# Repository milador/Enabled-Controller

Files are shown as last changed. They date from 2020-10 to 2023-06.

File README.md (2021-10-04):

# Enabled Controller

Enabled Controller Wireless is an open-source switch interface that enables those with limited or no hand movement to be able to use Adaptive switches and analog joysticks as inputs to operate their computers, smartphones, and game consoles.

<p align="center">
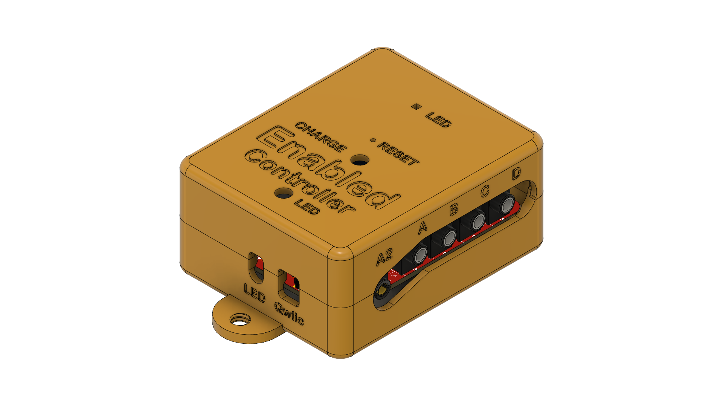
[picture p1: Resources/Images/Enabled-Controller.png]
Enabled Controller

</p>

The device offers up to eight switch input enclosures through eight 3.5mm audio jacks and four analog inputs through two 3.5mm headphone jacks. The two 3.5mm headphone jacks can be used to connect up to two X-Y analog joysticks.

The internal RGB led of ItsyBitsy and external NeoPixel is used to provide visual feedback for each action.

## Assembly Instructions Manual

The <a href="https://github.com/milador/Enabled-Controller/blob/master/Documentation/Build_Manuals/Enabled_Controller_Instructions_Manual.pdf">Assembly Instructions Manual</a> is available to download.

## User Manual

### Enabled Controller USB User Manual

<a href="https://github.com/milador/Enabled-Controller/blob/master/Documentation/User_Manuals/Enabled_Controller_USB_User_Manual.pdf">Enabled_Controller_USB_User_Manual.pdf</a>

### Enabled Controller Joystick User Manual 

<a href="https://github.com/milador/Enabled-Controller/blob/master/Documentation/User_Manuals/Enabled_Controller_Joystick_User_Manual.pdf">Enabled_Controller_Joystick_User_Manual.pdf</a>

## Parts

The <a href="https://github.com/milador/Enabled-Controller/blob/master/Components/Enabled_Controller_BOM.csv">BOM</a> file is available to download.

## Software

### Enabled_Controller_USB_Software.ino  

The <a href="https://raw.githubusercontent.com/milador/Enabled-Controller/master/Software/Arduino/Enabled_Controller_USB_Software/Enabled_Controller_USB_Software.ino">Enabled_Controller_USB_Software.ino</a> allows you to use adaptive switches as input method via keyboard/mouse HID profiles. 

### Enabled_Controller_Joystick_Software.ino  

The <a href="https://raw.githubusercontent.com/milador/Enabled-Controller/master/Software/Arduino/Enabled_Controller_Joystick_Software/Enabled_Controller_Joystick_Software.ino">Enabled_Controller_Joystick_Software.ino</a> allows you to use adaptive switches as input method via joystick HID profiles. 

## Hardware 

### PCB Design 

The <a href="https://github.com/milador/Enabled-Controller/tree/master/Hardware/PCB">PCB files</a> including both PCB Eagle design files and generated gerber files are available to download.

Front PCB:
<p align="center">
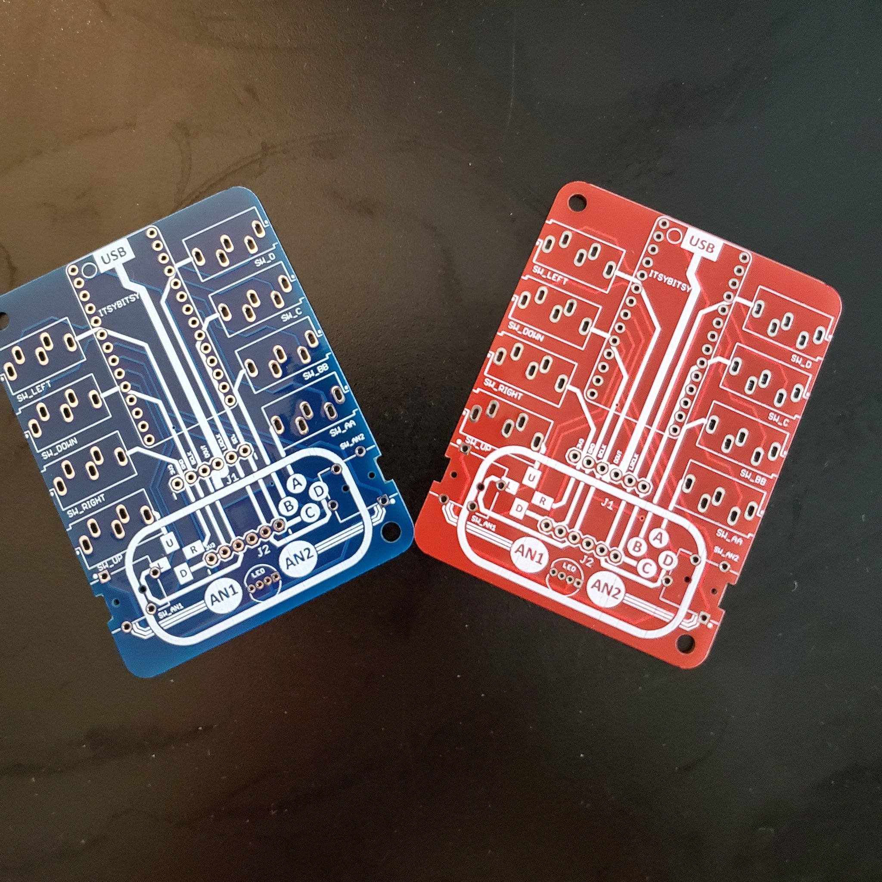
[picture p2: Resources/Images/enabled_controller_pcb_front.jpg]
Front PCB

</p>

Back PCB:
<p align="center">
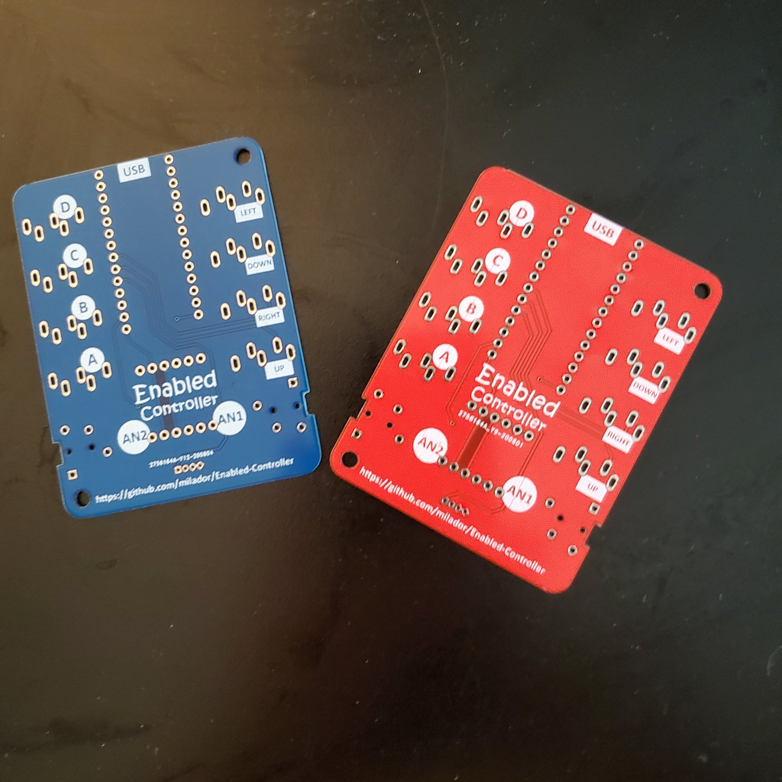
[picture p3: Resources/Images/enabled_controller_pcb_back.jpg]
Back PCB

</p>

Assembled:
<p align="center">
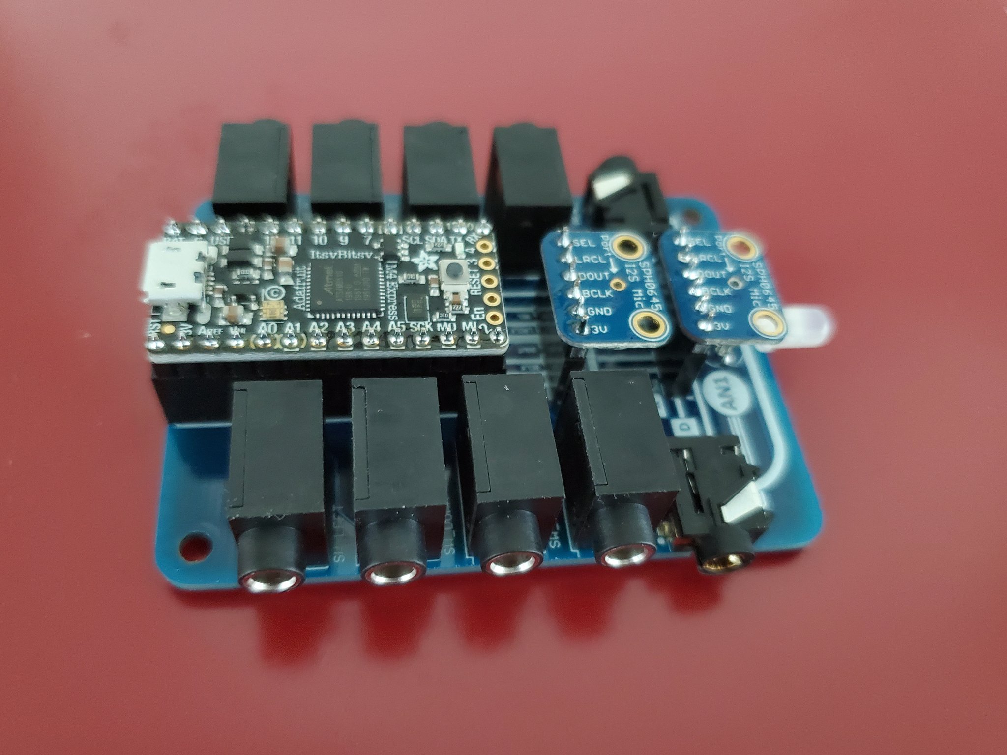
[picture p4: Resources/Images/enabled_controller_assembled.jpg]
Assembled PCB

</p>

Assembly Animation:

https://www.youtube.com/watch?v=7AMCL-cITrQ

### Enclosure

The <a href="https://github.com/milador/Enabled-Controller/tree/master/Hardware/Enclosure">Enclosure files</a> including both STL and STEP enclosure files are available to download.

<p align="center">
Enabled Controller
</p>

## License

### Creative Commons Attribution-NonCommercial-ShareAlike (CC-BY-NC-SA)

Copyright (c) 2020 Milador

A creative commons license that bans commercial use and requires you to release any modified works under this license.

<p align="center">
CC-BY-NC-SA
</p>

<br />This work is licensed under a <a rel="license" href="http://creativecommons.org/licenses/by-nc-sa/3.0/">Creative Commons Attribution-NonCommercial-ShareAlike 3.0 Unported License</a>.

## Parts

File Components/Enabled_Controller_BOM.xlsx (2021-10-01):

Index | Quantity | Digikey Part Number | Manufacturer Part Number | Description | Price (CAD) | Unit Price (CAD) | Link
1 | 1 | 1528-2554-ND | 3727 | ITSYBITSY M0 EXPRESS ATSAMD21 | 16.15 | 16.15 | https://www.digikey.ca/en/products/detail/adafruit-industries-llc/3727/8346575
2 | 1 | 1568-1213-ND | COM-12986 | ADDRESS LED DISC SER RGB 5MM 5PC | 3.99 | 3.99 | https://www.digikey.ca/en/products/detail/COM-12986/1568-1213-ND/5673799
3 | 2 | S7047-ND | PPPC141LFBN-RC | CONN HDR 14POS 0.1 GOLD | 1.28 | 1.28 | https://www.digikey.ca/en/products/detail/PPPC141LFBN-RC/S7047-ND/810186
4 | 8 | CP1-3535NG-ND | SJ1-3535NG | CONN JACK STEREO 3.5MM R/A | 1.61 | 1.61 | https://www.digikey.ca/product-detail/en/cui-inc/SJ1-3535NG/CP1-3535NG-ND
5 | 2 | CP-43514-ND | SJ-43514 | CONN JACK 4COND 3.5MM | 1.43 | 1.43 | https://www.digikey.ca/en/products/detail/SJ-43514/CP-43514-ND/368146
6 | 2 | 36-4708-ND | 4708 | HEX NUT 0.217" STEEL M3 | 0.23 | 0.23 | https://www.digikey.ca/en/products/detail/keystone-electronics/4708/4499301
7 | 2 | 335-1148-ND | RM3X10MM 2701 | MACH SCREW PAN HEAD PHILLIPS M3 | 0.92 | 0.92 | https://www.digikey.ca/en/products/detail/apm-hexseal/RM3X10MM-2701/3712296
8 | 1 | PRT-14417-ND | PRT-14417 | QWIIC JST CONNECTOR - SMD 4-PIN | 0.68 | 0.68 | https://www.digikey.ca/en/products/detail/sparkfun-electronics/PRT-14417/7652746
 |  |  |  |  | Total Price (CAD) | 41.42

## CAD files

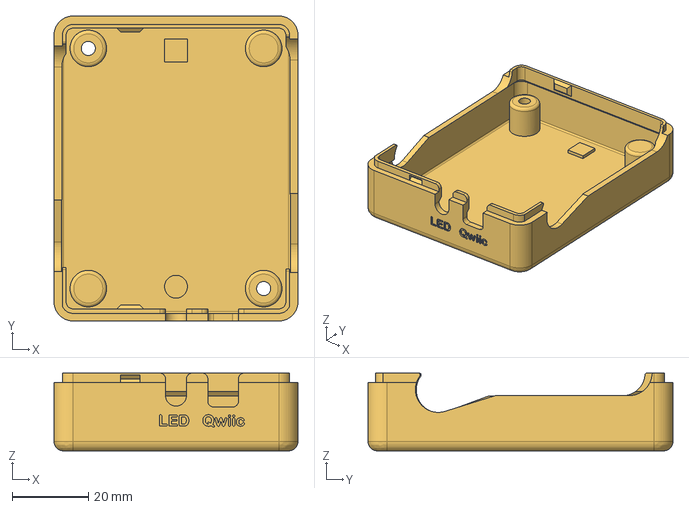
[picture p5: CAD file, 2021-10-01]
Hardware/Enclosure/STEP/Enabled_Controller_Bottom.step
64.0 x 80.0 x 20.4 mm

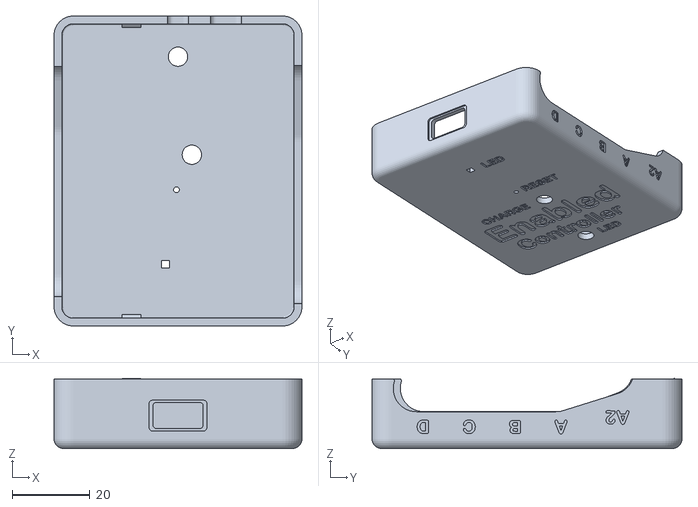
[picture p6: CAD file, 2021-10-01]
Hardware/Enclosure/STL/Enabled_Controller_Top.stl
64.0 x 80.0 x 18.1

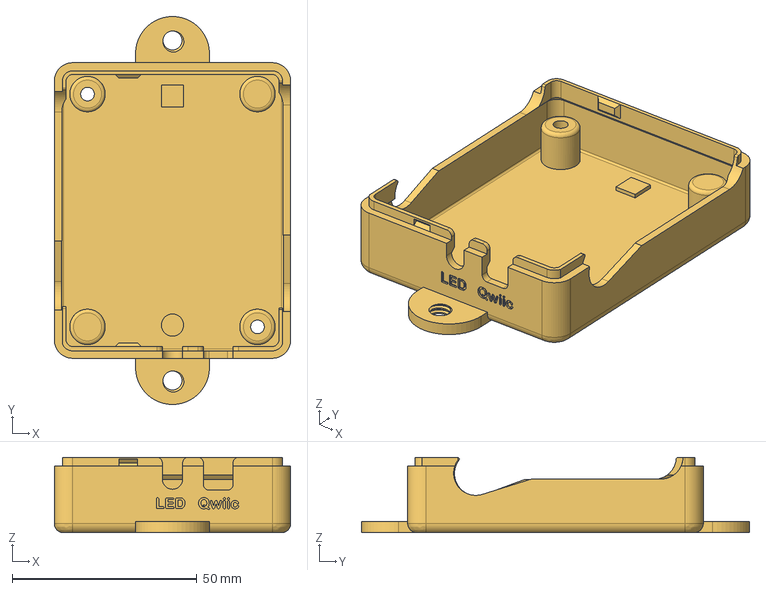
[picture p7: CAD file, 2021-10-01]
Hardware/Enclosure/STEP/Enabled_Controller_Bottom_With_Mount.step
64.0 x 105.0 x 20.4 mm

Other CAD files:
Hardware/Enclosure/STL/Enabled_Controller_Bottom.stl
Hardware/Enclosure/STL/Enabled_Controller_Bottom_With_Mount.stl

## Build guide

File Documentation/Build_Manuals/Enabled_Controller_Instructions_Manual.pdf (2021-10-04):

# ENABLED-CONTROLLER INSTRUCTIONS MANUAL

An Accessible Adaptive Switch Interface

## Version 1.2

https://github.com/milador/Enabled-Controller

1

## Contents

Components List | 2
Software | 3
Installing Arduino IDE | 3
Installing Arduino Libraries | 3
USB Version | 3
Board Support Packages | 3
Required Software and libraries | 4
Uploading Software | 5
Joystick Version | 6
Board Support Packages | 6
Required Software and libraries | 6
Uploading Software | 7
Hardware Assembly | 8
Printed circuit Board design | 8
Enclosure design | 8
Enabled-Controller Assembly | 9
Joystick Assembly | 36

2

## Components List

### 1. ADAFRUIT ITSY-BITSY M0 EXPRESS x 1

### 2. ADDRESS LED DISC SER RGB 5MM x 1

3. 14 POSITION HEADER x 2

### 4. CONN JACK STEREO 3.5MM R/A x 8

### 5. CONN JACK 4COND 3.5MM x 2

### 6. HEX NUT 0.217" STEEL M3 x 2

### 7. MACH SCREW PAN HEAD PHILLIPS M3 x 2

### 8. QWIIC JST CONNECTOR - SMD 4-PIN x 1

The bill of materials can also be downloaded from GitHub repository under main directory.

https://github.com/milador/Enabled-

Controller/blob/master/Components/Enabled_Controller_BOM.csv (https://github.com/milador/Enabled-Controller/blob/master/Components/Enabled_Controller_BOM.csv)

3

## Software

The Enabled-Controller USB software can be downloaded from the GitHub repository under software directory.

https://github.com/milador/Enabled-Controller/tree/master/Software/Arduino

The Enabled-Controller USB software is offered in the following flavors:

### 1. USB Version: Adafruit ItsyBitsy M0 Express

### 2. Joystick Version: Adafruit ItsyBitsy M0 Express

### Installing Arduino IDE

The Arduino IDE is required to compile and upload the source code to the MCU in your Adafruit ItsyBitsy board. You can download and install the Arduino from official Arduino website that you can find using following link:

https://www.arduino.cc/en/software

### Installing Arduino Libraries

The following instructions on how to install additional Arduino libraries helps you to get started with setting up Arduino IDE with required libraries and dependencies.

https://www.arduino.cc/en/guide/libraries

### USB Version

Board Support Packages
You can find the official instructions to install Board Support Packages on Adafruit website using following link:

https://learn.adafruit.com/introducing-itsy-bitsy-m0/setup

Alternatively, you can perform following instructions to install Board Support Packages:

1. Open and start the Arduino IDE.
2. Go to File > Preferences.

### 3. Add following link as a new line under Additional Board Manager URLs

- https://www.adafruit.com/package_adafruit_index.json

### 4. Restart the Arduino IDE 5. Open the Boards Manager option from the Tools > Board menu and install Adafruit SAMD

Boards by Adafruit
6. Wait until the IDE finishes installing the cross-compiling toolchain and tools associated with Board Support Package. This may take few minutes.
7. That’s it! The installation of Board Support Packages is finished.

4

Required Software and libraries
The USB version of the software requires the following files and libraries:
- StopWatch library (https://github.com/RobTillaart/Stopwatch_RT)
- EasyMorse library (https://github.com/milador/EasyMorse)
- Adafruit_NeoPixel library (https://github.com/adafruit/Adafruit_NeoPixel)
- Enabled_Controller_USB_Software.ino (https://raw.githubusercontent.com/milador/Enabled-Controller/master/Software/Arduino/Enabled_Controller_USB_Software/Enabled_Controller_USB_Software.ino)

StopWatch library helps to calculate the reaction time and timeout in the morse code interface.

The EasyMorse library is used to enable the end user to use morse code or a sequence of dots and dashes as input method.

Enabled-Controller is using Adafruit_NeoPixel library to provide visual feedback using RGB LED.

You can use the following instructions to download and install the required libraries:

1. Visit the StopWatch library (https://github.com/RobTillaart/Stopwatch_RT) github repository page.
2. Click on Code > Download Zip to download StopWatch library.

### 3. Extract Stopwatch_RT-master.zip file 4. Rename Stopwatch_RT-master folder to Stopwatch folder under Stopwatch_RT-master

subdirectory.
5. Copy or move Stopwatch folder to Arduino installation library subdirectory. As an example: This is found under C:\Program Files (x86)\Arduino\libraries in windows 10.
6. Visit the EasyMorse library (https://github.com/milador/EasyMorse) github repository page.
7. Click on Code > Download Zip to download EasyMorse library.

### 8. Extract EasyMorse.zip file

9. Rename EasyMorse-master folder to EasyMorse folder under EasyMorse-master subdirectory.
10. Copy or move EasyMorse folder to Arduino installation library subdirectory. As an example: This is found under C:\Program Files (x86)\Arduino\libraries in windows 10.
11. Visit the Enabled_Controller_USB_Software.ino (https://raw.githubusercontent.com/milador/Enabled-Controller/master/Software/Arduino/Enabled_Controller_USB_Software/Enabled_Controller_USB_Software.ino) raw source code file under Enabled-Controller github repository page.

### 12. Right click on the source code or any place on this page and select Save Page As…

13. Select the directory you would like to save the software in your computer.

### 14. Change File name from Enabled_Controller_USB_Software to

Enabled_Controller_USB_Software.ino
15. Change Save as type to All Files.
16. Click on Save button.
17. Open the directory you selected in step 13.

### 18. Double left click or open Enabled_Controller_USB_Software file 19. Arduino IDE will ask your permission to create a new sketch folder named

Enabled_Controller_USB_Software and move Enabled_Controller_USB_Software.ino under this folder.
20. Click on the Ok button.
21. Arduino IDE should now open the Enabled_Controller_USB_Software.ino file automatically.

5

Uploading Software
Note: Make sure all files are included in your local copy of Software directory before uploading it to the Adafruit ItsyBitsy board. The libraries can be installed in Arduino libraries.

You can go ahead and upload the downloaded .ino code to Adafruit ItsyBitsy board using Arduino IDE once all the necessary libraries are installed.

1. Start the Arduino IDE.

### 2. Open Enabled_Controller_USB_Software.ino

3. Select the Board under Tools > Board > Adafruit SAMD Boards as Adafruit ItsyBitsy M0 Express

### 4. Select the correct port number under Tools > Port which should show COM XX (Adafruit

ItsyBitsy M0 Express)

Note: It’s very important to make sure the correct Board and port number are selected as selecting the wrong board may result problems with bootloader of Adafruit ItsyBitsy board.

5. Press the Verify button to make sure there is no problem with the software and libraries.

### 6. Press Upload button

You can now go ahead and upload the software. Arduino IDE will show you a Done Uploading message indicating the software is uploaded to your Enabled-Controller.

The LED on the Enabled-Controller main board blinks two times in teal to indicate the start of initialization process has been started and it will blink again two times in green to indicate end of the initialization process.

You can also open the Serial Monitor in Arduino IDE on 115200 baud-rate to read initialization information about the version of software.

6

### Joystick Version

Board Support Packages
You can find the official instructions to install Board Support Packages on Adafruit website using following link:

https://learn.adafruit.com/introducing-itsy-bitsy-m0/setup

Alternatively, you can perform following instructions to install Board Support Packages:

1. Open and start the Arduino IDE.
2. Go to File > Preferences.

### 3. Add following link as a new line under Additional Board Manager URLs

- https://www.adafruit.com/package_adafruit_index.json

### 4. Restart the Arduino IDE 5. Open the Boards Manager option from the Tools > Board menu and install Adafruit SAMD

Boards by Adafruit
6. Wait until the IDE finishes installing the cross-compiling toolchain and tools associated with Board Support Package. This may take few minutes.
7. That’s it! The installation of Board Support Packages is finished.

Required Software and libraries
The Joystick version of the software requires the following files and libraries:
- StopWatch library (https://github.com/RobTillaart/Stopwatch_RT)
- Joystick library (SAMD Version)
- Adafruit_NeoPixel library (https://github.com/adafruit/Adafruit_NeoPixel)
- Enabled_Controller_Joystick_Software.ino (https://raw.githubusercontent.com/milador/Enabled-Controller/master/Software/Arduino/Enabled_Controller_Joystick_Software/Enabled_Controller_Joystick_Software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)

StopWatch library helps to calculate the reaction time and timeout in the morse code interface.

The joystick library is used to turn Enabled Controller into a joystick USB HID device which can be used for gaming. Please make sure you install the SAMD version of the joystick library.

Enabled Controller is using Adafruit_NeoPixel library to provide visual feedback using RGB LED.

You can use the following instructions to download and install the required libraries:

1. Visit the StopWatch library (https://github.com/RobTillaart/Stopwatch_RT) github repository page.
2. Click on Code > Download Zip to download StopWatch library.

### 3. Extract Stopwatch_RT-master.zip file 4. Rename Stopwatch_RT-master folder to Stopwatch folder under Stopwatch_RT-master

subdirectory.
5. Copy or move Stopwatch folder to Arduino installation library subdirectory. As an example: This is found under C:\Program Files (x86)\Arduino\libraries in windows 10.
6. Visit the Joystick library (SAMD Version) github repository page.
7. Click on Code > Download Zip to download ArduinoJoystickLibrary-samd_patch library.

### 8. Extract ArduinoJoystickLibrary-samd_patch.zip file

7

9. Copy or move Joystick folder under ArduinoJoystickLibrary-samd_patch-master subdirectory to Arduino installation library subdirectory. As an example: This is found under C:\Program Files (x86)\Arduino\libraries in windows 10.
10. Visit the Enabled_Controller_Joystick_Software.ino (https://raw.githubusercontent.com/milador/Enabled-Controller/master/Software/Arduino/Enabled_Controller_Joystick_Software/Enabled_Controller_Joystick_Software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) raw source code file under Enabled-Controller github repository page.

### 11. Right click on the source code or any place on this page and select Save Page As…

12. Select the directory you would like to save the software in your computer.

### 13. Change File name from Enabled_Controller_Joystick_Software to

Enabled_Controller_Joystick_Software.ino
14. Change Save as type to All Files.
15. Click on Save button.
16. Open the directory you selected in step 12.

### 17. Double left click or open Enabled_Controller_Joystick_Software file 18. Arduino IDE will ask your permission to create a new sketch folder named

Enabled_Controller_Joystick_Software and move Enabled_Controller_Joystick_Software.ino under this folder.
19. Click on the Ok button.
20. Arduino IDE should now open the Enabled_Controller_Joystick_Software.ino file automatically.

Uploading Software
Note: Make sure all files are included in your local copy of Software directory before uploading it to the Adafruit ItsyBitsy board. The libraries can be installed in Arduino libraries.

You can go ahead and upload the downloaded .ino code to Adafruit ItsyBitsy board using Arduino IDE once all the necessary libraries are installed.

### 1. Start the Arduino IDE 2. Open Enabled_Controller_Joystick_Software.ino

3. Select the Board under Tools > Board > Adafruit SAMD Boards as Adafruit ItsyBitsy M0 Express

### 4. Select the correct port number under Tools > Port which should show COM XX (Adafruit

ItsyBitsy M0 Express)

Note: It’s very important to make sure the correct Board and port number are selected as selecting the wrong board may result problems with bootloader of Adafruit ItsyBitsy board.

5. Press the Verify button to make sure there is no problem with the software and libraries.

### 6. Press Upload button

You can now go ahead and upload the software. Arduino IDE will show you a Done Uploading message indicating the software is uploaded to your Enabled-Controller.

The LED on the Enabled-Controller main board blinks two times in teal to indicate the start of initialization process has been started and it will blink again two times in green to indicate end of the initialization process.

You can also open the Serial Monitor in Arduino IDE on 115200 baud-rate to read initialization information about the version of software.

8

## Hardware Assembly

### Printed circuit Board design

The printed circuit boards (PCB) can be downloaded from GitHub repository under Hardware directory.

https://github.com/milador/Enabled-Controller/tree/master/Hardware/PCB

### Enclosure design

The enclosure/housing files in STL format can be downloaded from GitHub repository under Hardware directory.

https://github.com/milador/Enabled-Controller/tree/master/Hardware/Enclosure

Please print the following STL files:

- 1 x Enabled_Controller_Top.stl
- 1 x Enabled_Controller_Bottom.stl or Enabled_Controller_Bottom_With_Mount.stl

9

### Enabled-Controller Assembly

Step 1: Enabled-Controller board x 1.

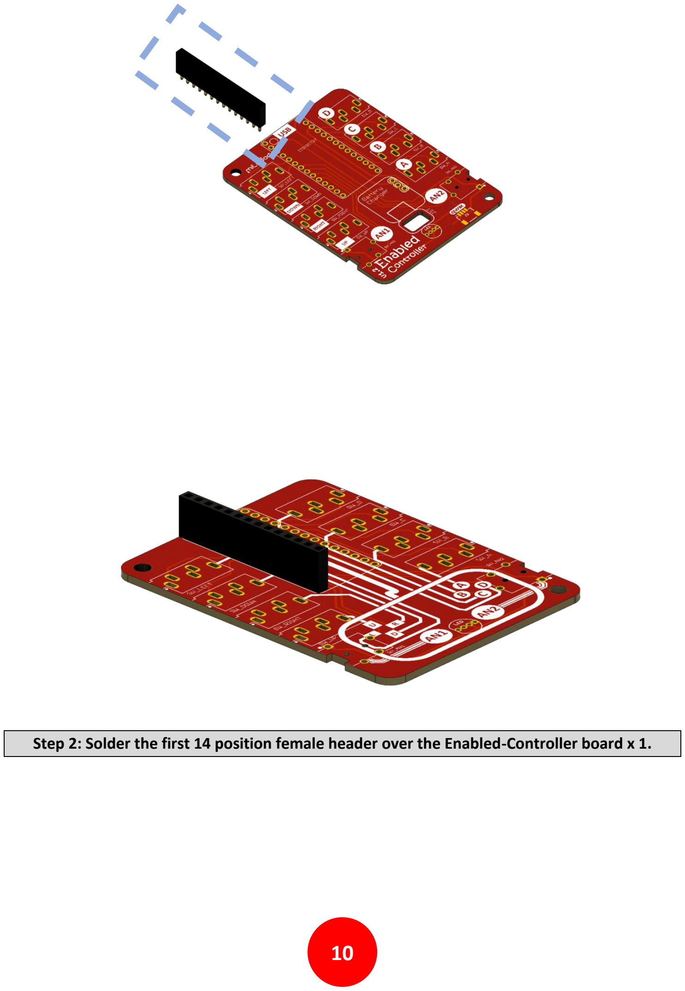
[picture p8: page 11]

10

Step 2: Solder the first 14 position female header over the Enabled-Controller board x 1.

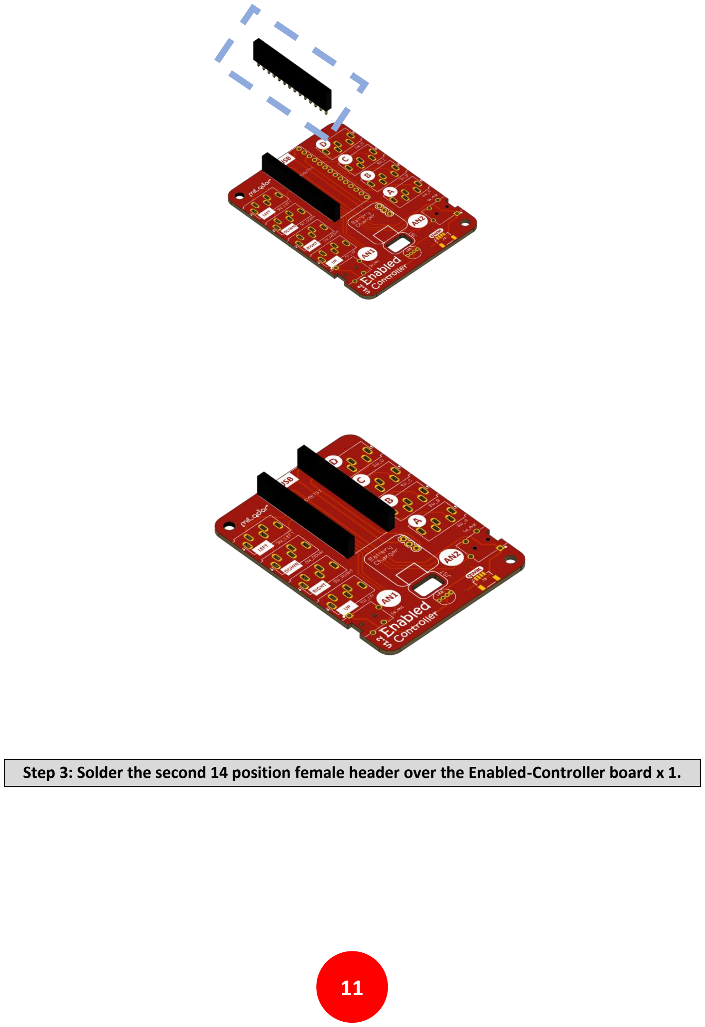
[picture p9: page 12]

11

Step 3: Solder the second 14 position female header over the Enabled-Controller board x 1.

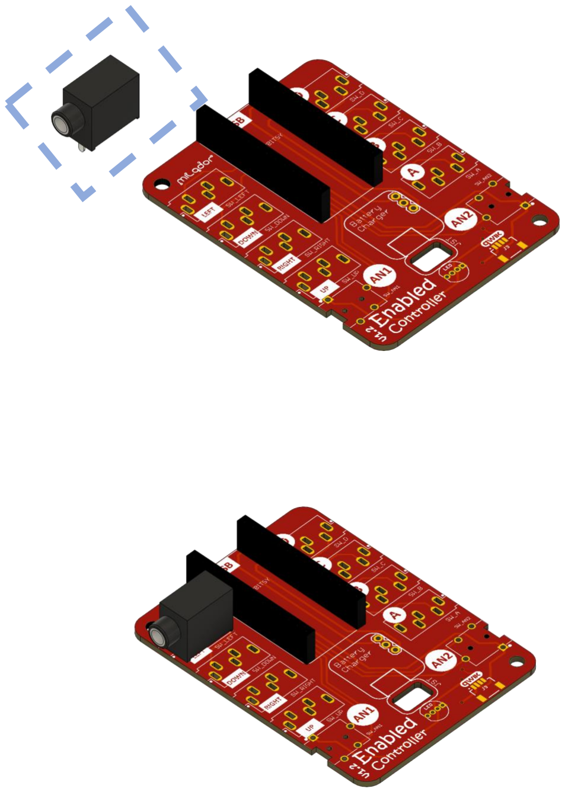
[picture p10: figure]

12

Step 4: Position a 3.5mm jack on the Left switch outline and solder the pins x 1.

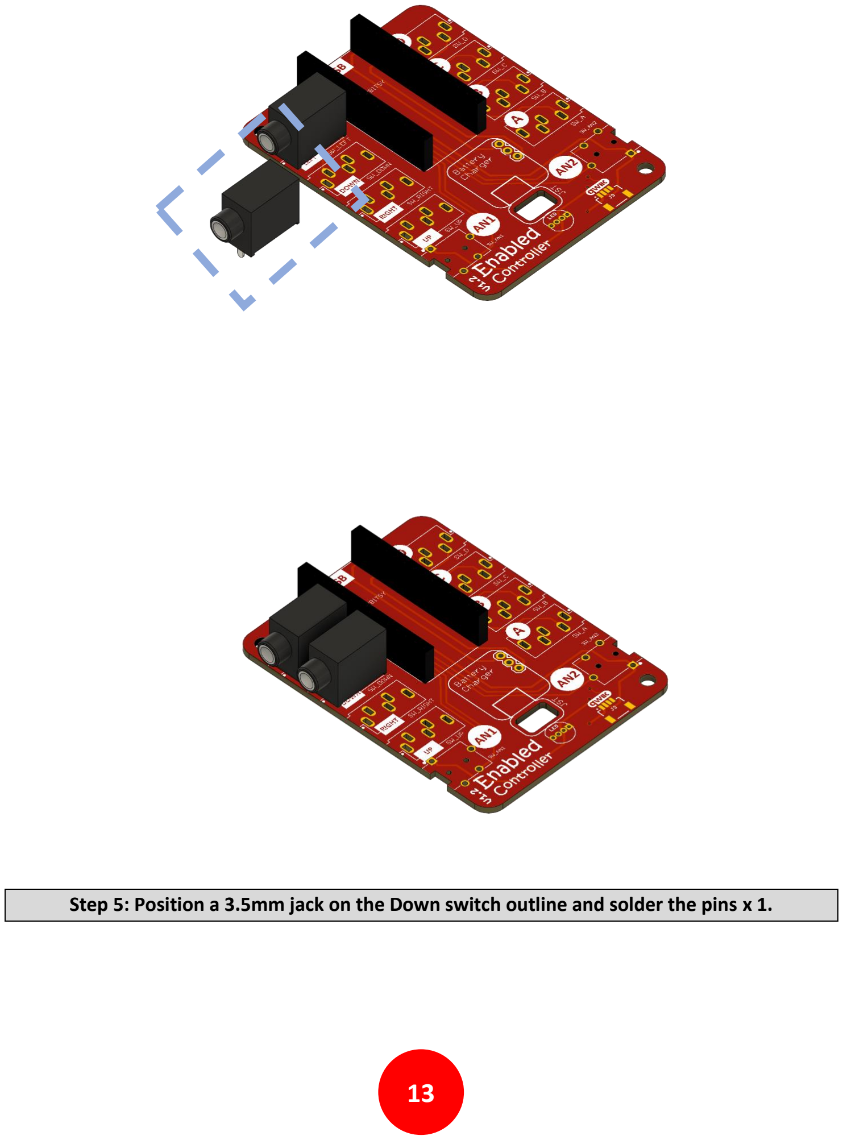
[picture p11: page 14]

13

Step 5: Position a 3.5mm jack on the Down switch outline and solder the pins x 1.

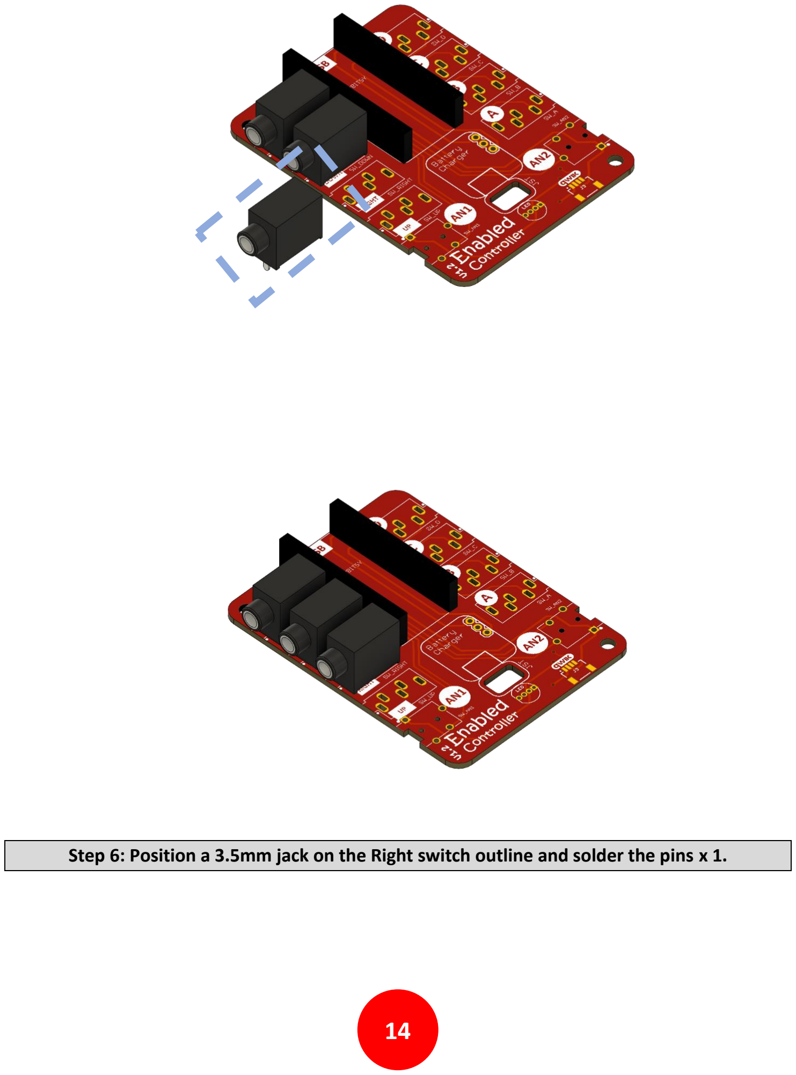
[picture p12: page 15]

14

Step 6: Position a 3.5mm jack on the Right switch outline and solder the pins x 1.

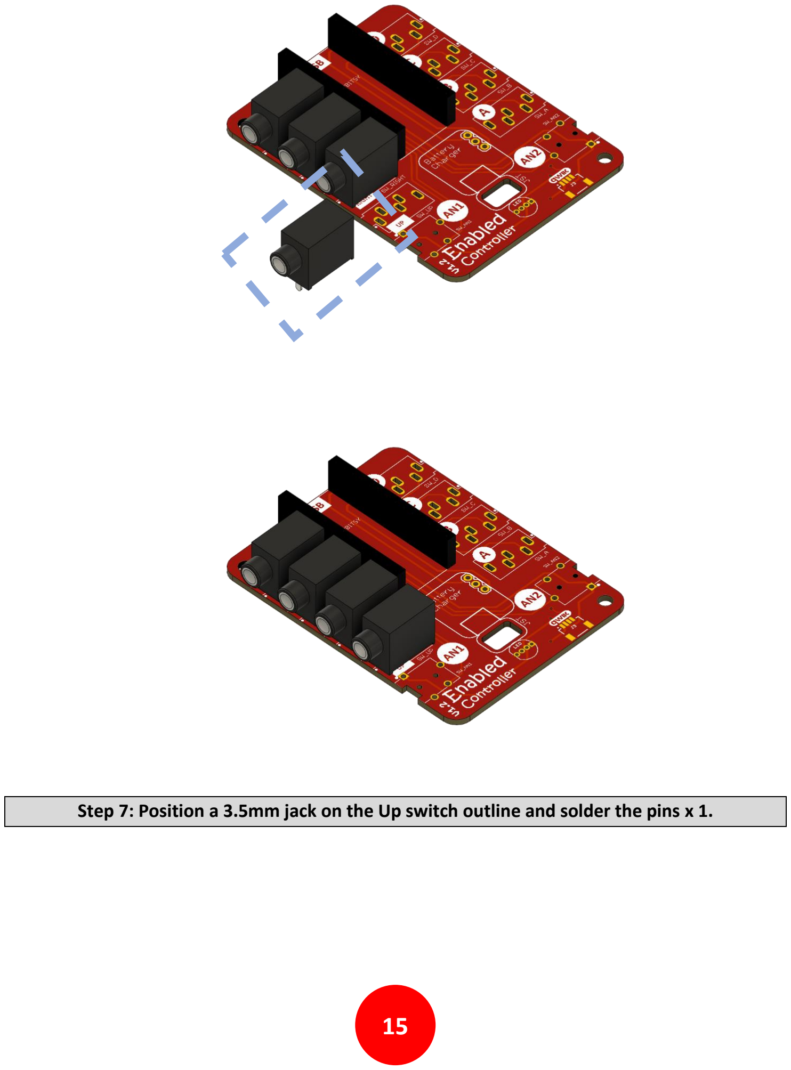
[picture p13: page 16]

15

Step 7: Position a 3.5mm jack on the Up switch outline and solder the pins x 1.

16

Step 8: Position a 4 Conductor 3.5mm jack on the AN1 switch outline and solder the pins x 1.

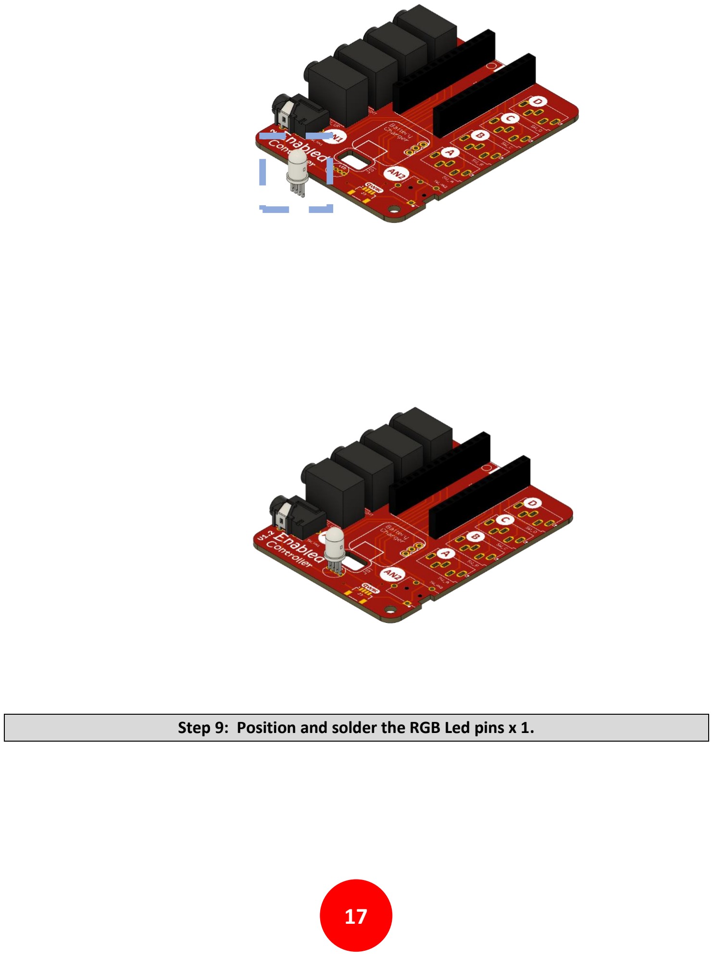
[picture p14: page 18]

17

Step 9: Position and solder the RGB Led pins x 1.

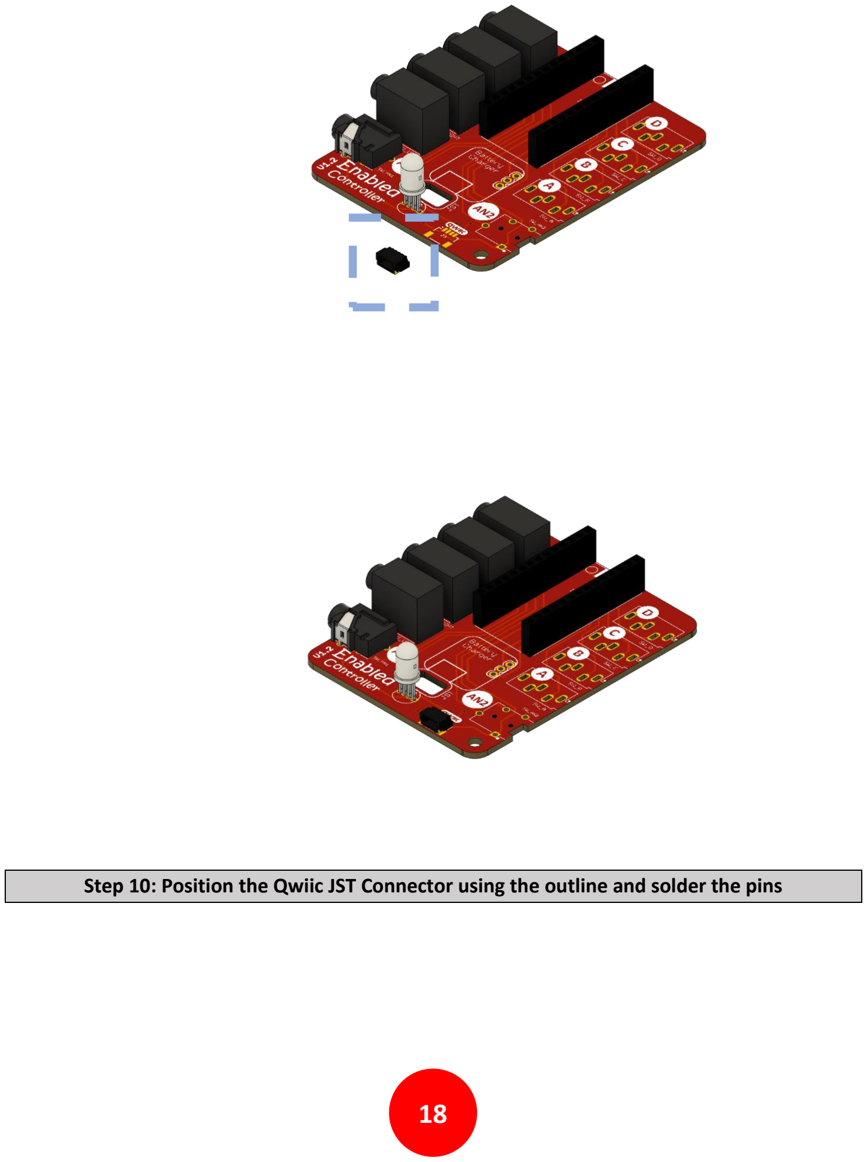
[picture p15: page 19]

18

Step 10: Position the Qwiic JST Connector using the outline and solder the pins

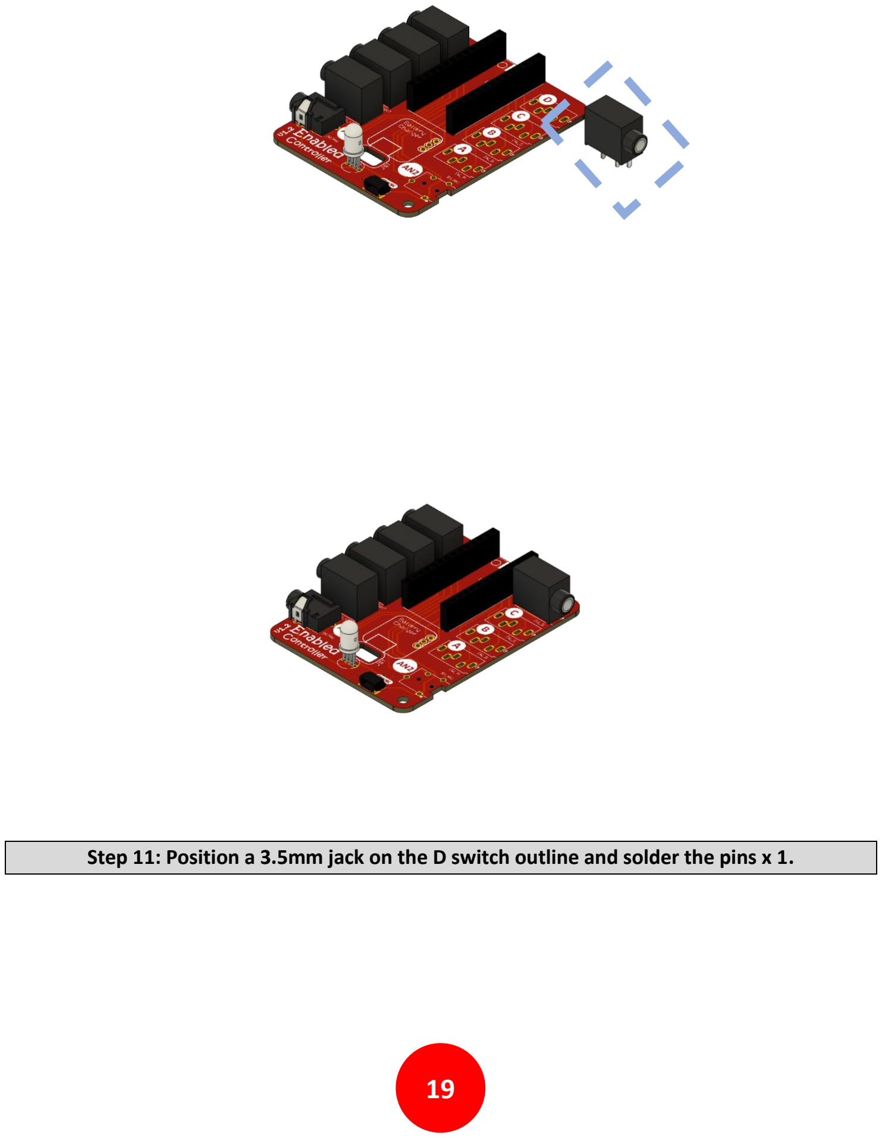
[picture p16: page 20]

19

Step 11: Position a 3.5mm jack on the D switch outline and solder the pins x 1.

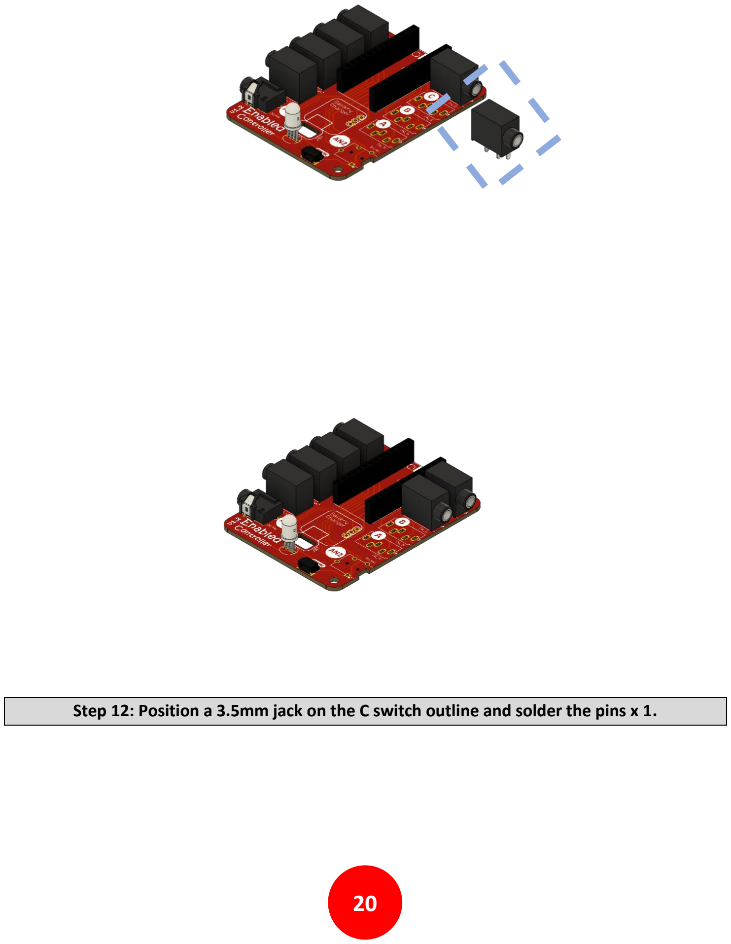
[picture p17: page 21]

20

Step 12: Position a 3.5mm jack on the C switch outline and solder the pins x 1.

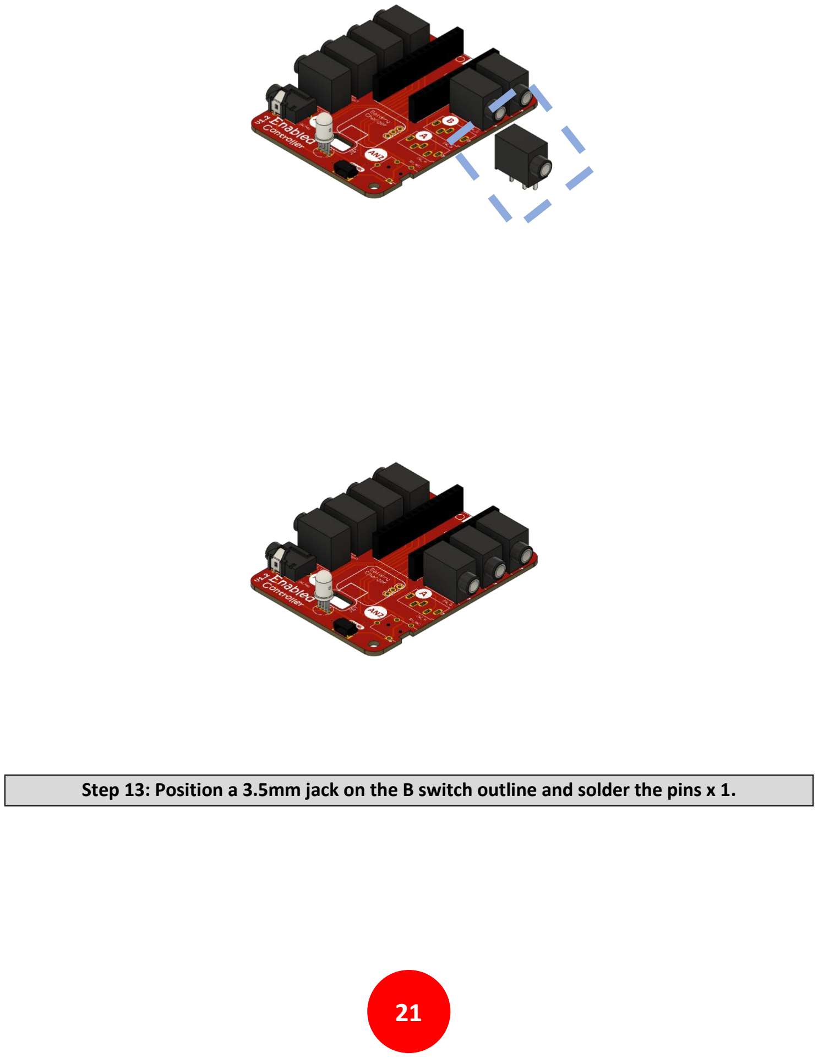
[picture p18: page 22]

21

Step 13: Position a 3.5mm jack on the B switch outline and solder the pins x 1.

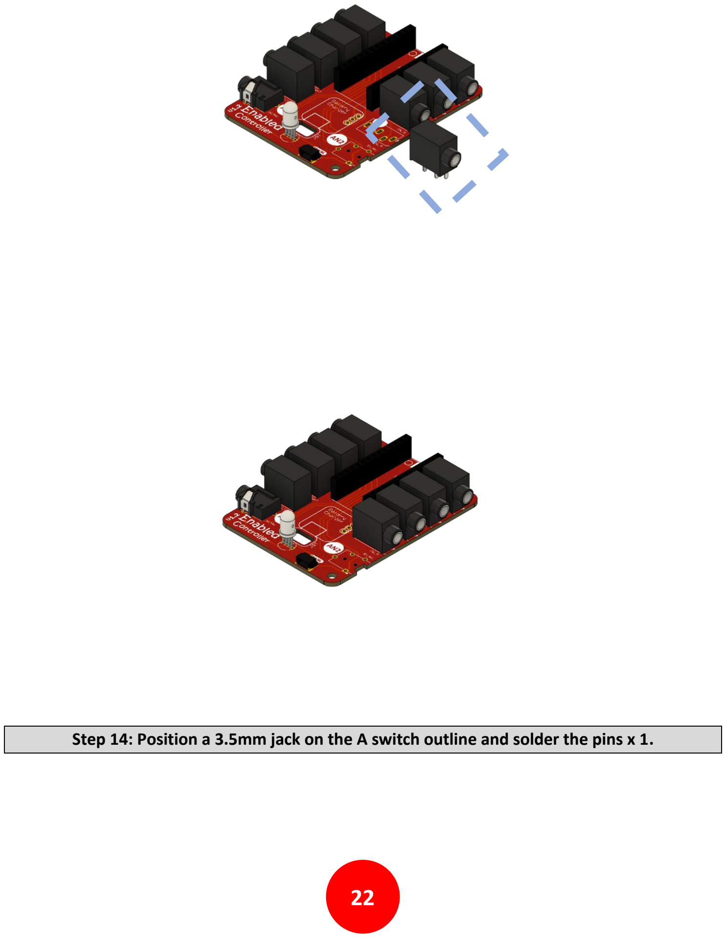
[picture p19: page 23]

22

Step 14: Position a 3.5mm jack on the A switch outline and solder the pins x 1.

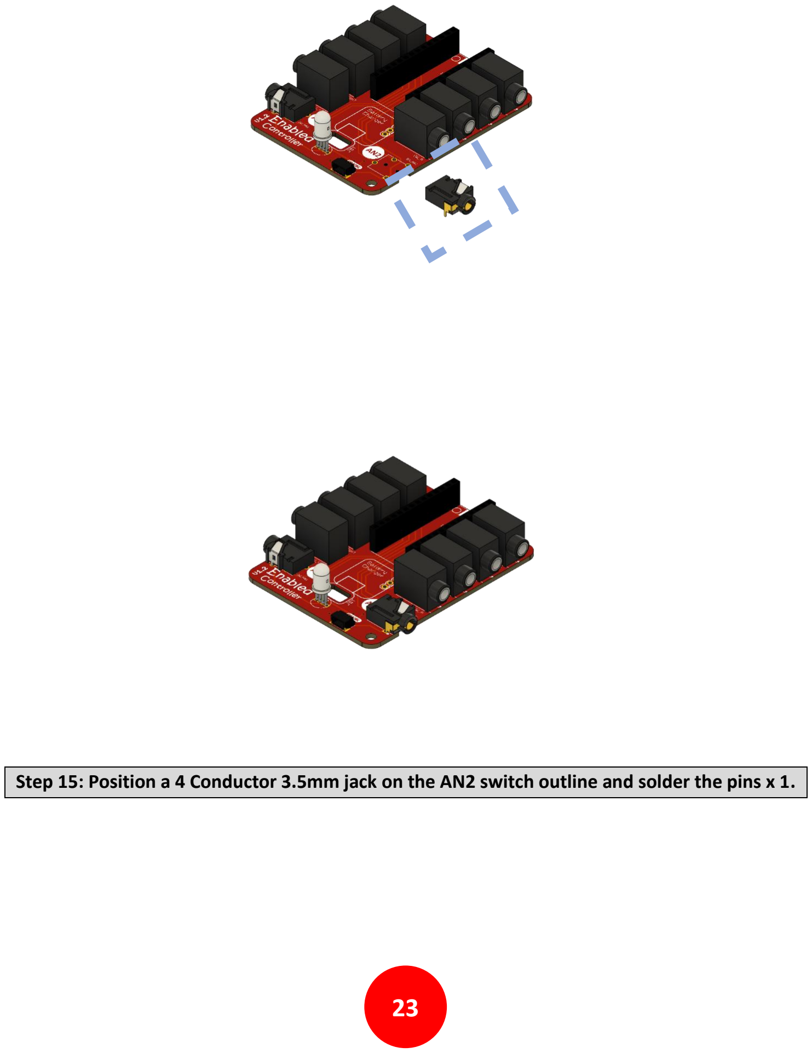
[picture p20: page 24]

23

Step 15: Position a 4 Conductor 3.5mm jack on the AN2 switch outline and solder the pins x 1.

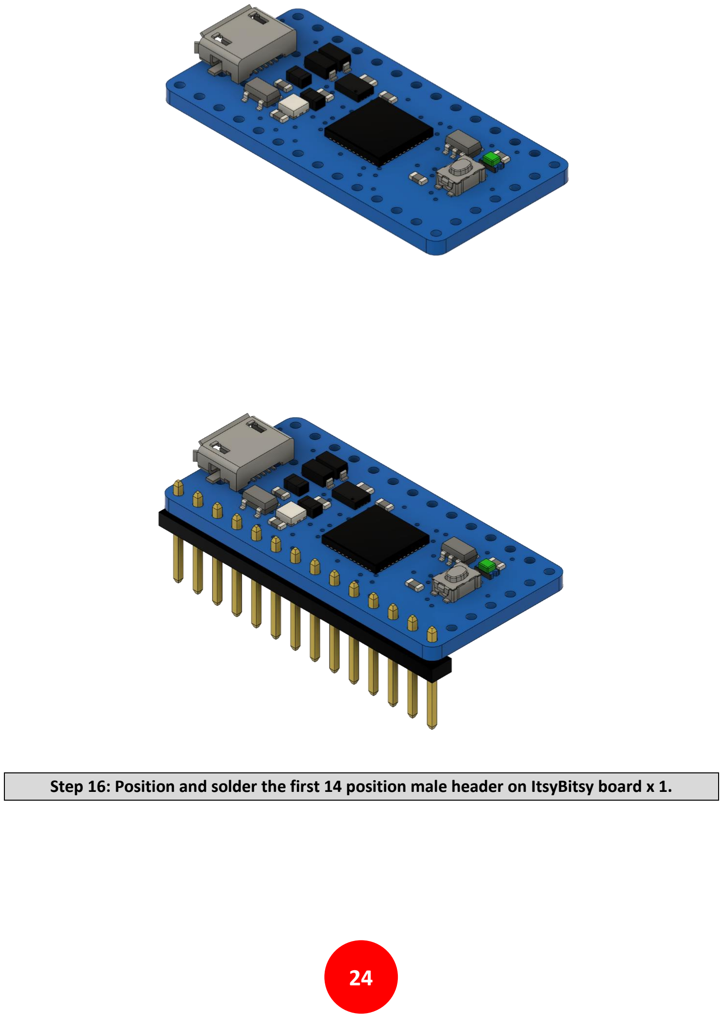
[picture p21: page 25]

24

Step 16: Position and solder the first 14 position male header on ItsyBitsy board x 1.

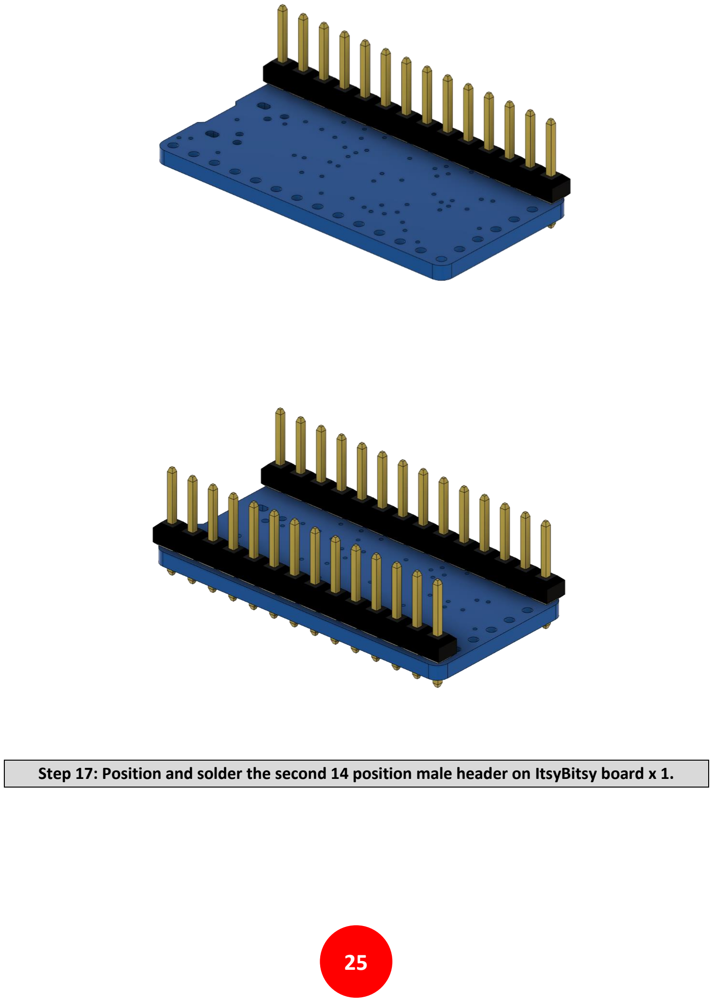
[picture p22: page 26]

25

Step 17: Position and solder the second 14 position male header on ItsyBitsy board x 1.

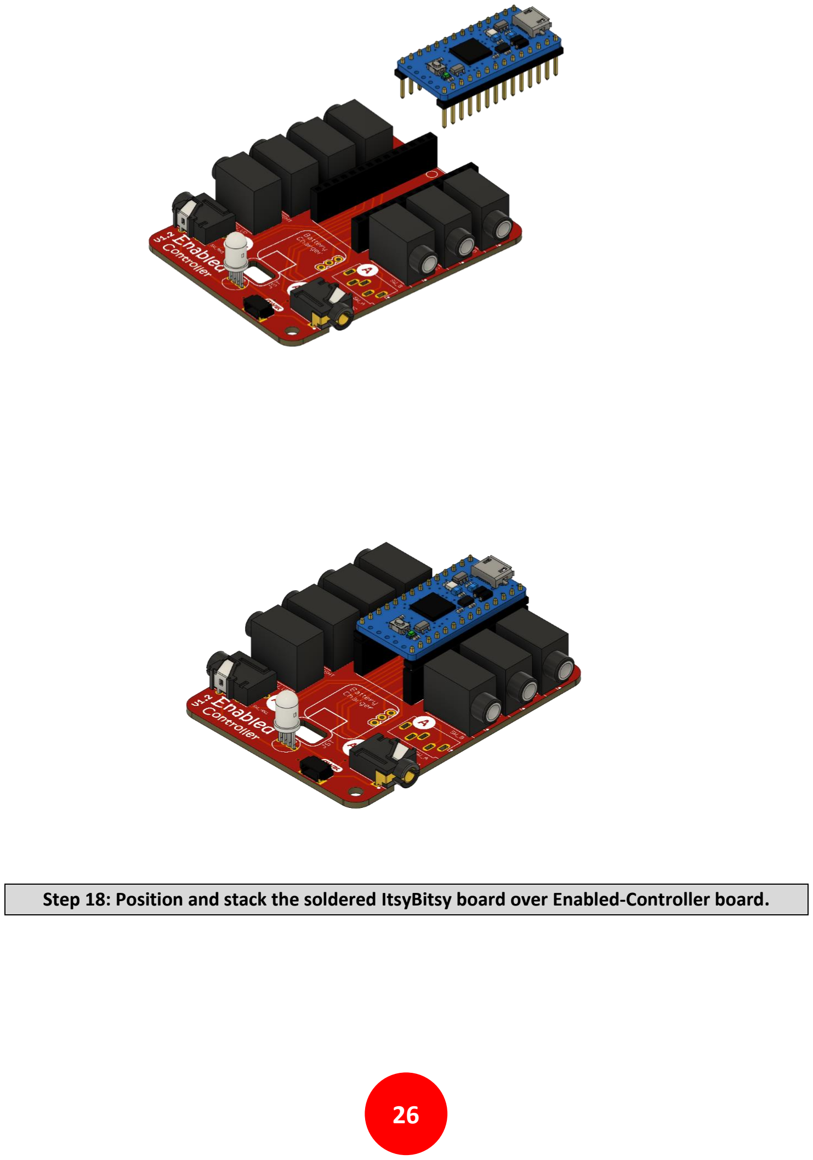
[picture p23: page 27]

26

Step 18: Position and stack the soldered ItsyBitsy board over Enabled-Controller board.

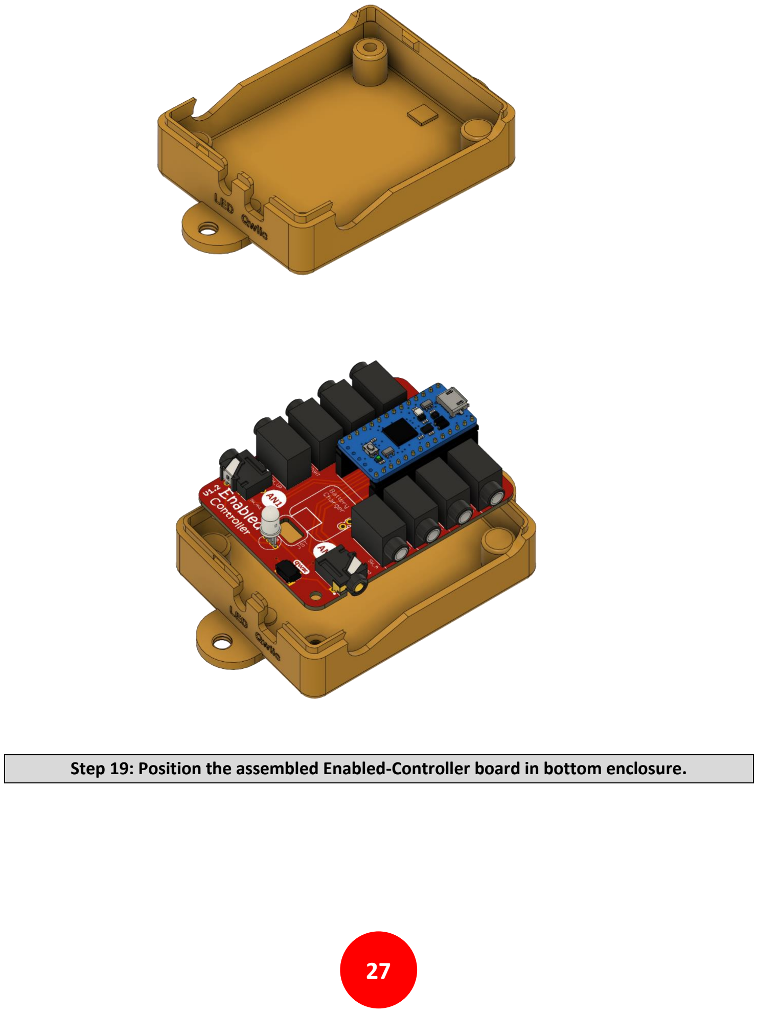
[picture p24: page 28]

27

Step 19: Position the assembled Enabled-Controller board in bottom enclosure.

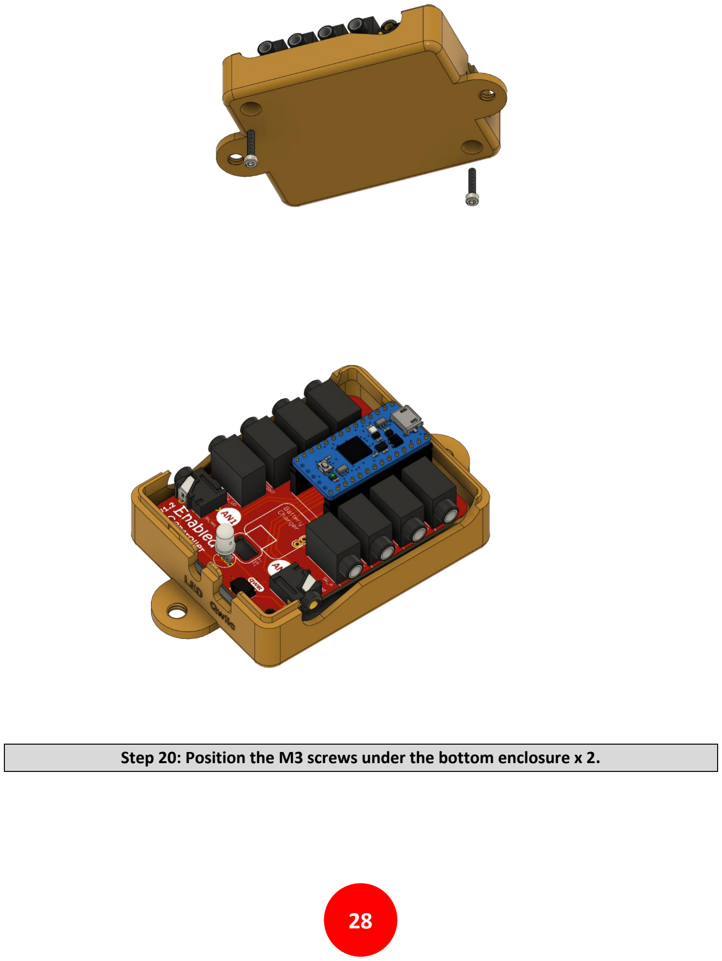
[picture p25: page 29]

28

Step 20: Position the M3 screws under the bottom enclosure x 2.

29

Step 21: Insert the M3 screws and push them through the Enabled-Controller drill holes x 2.

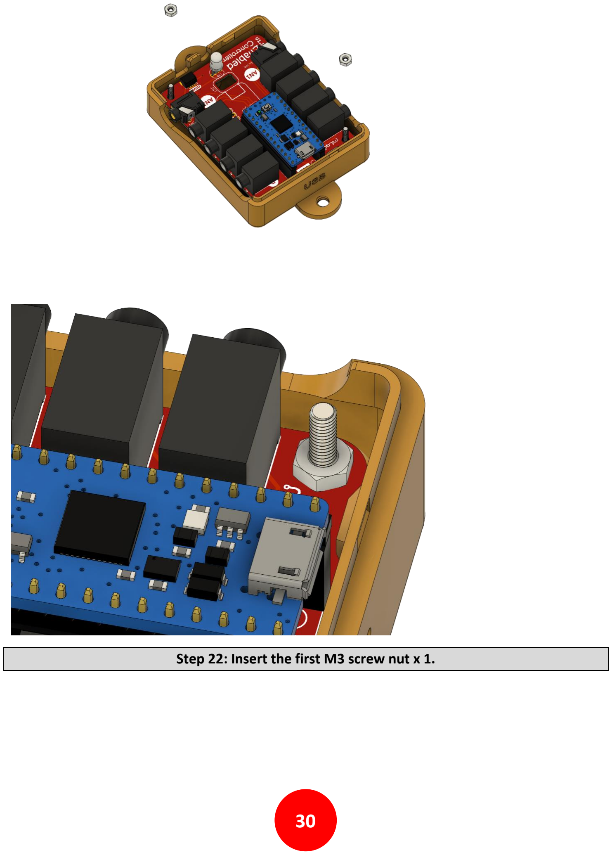
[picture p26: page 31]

30

Step 22: Insert the first M3 screw nut x 1.

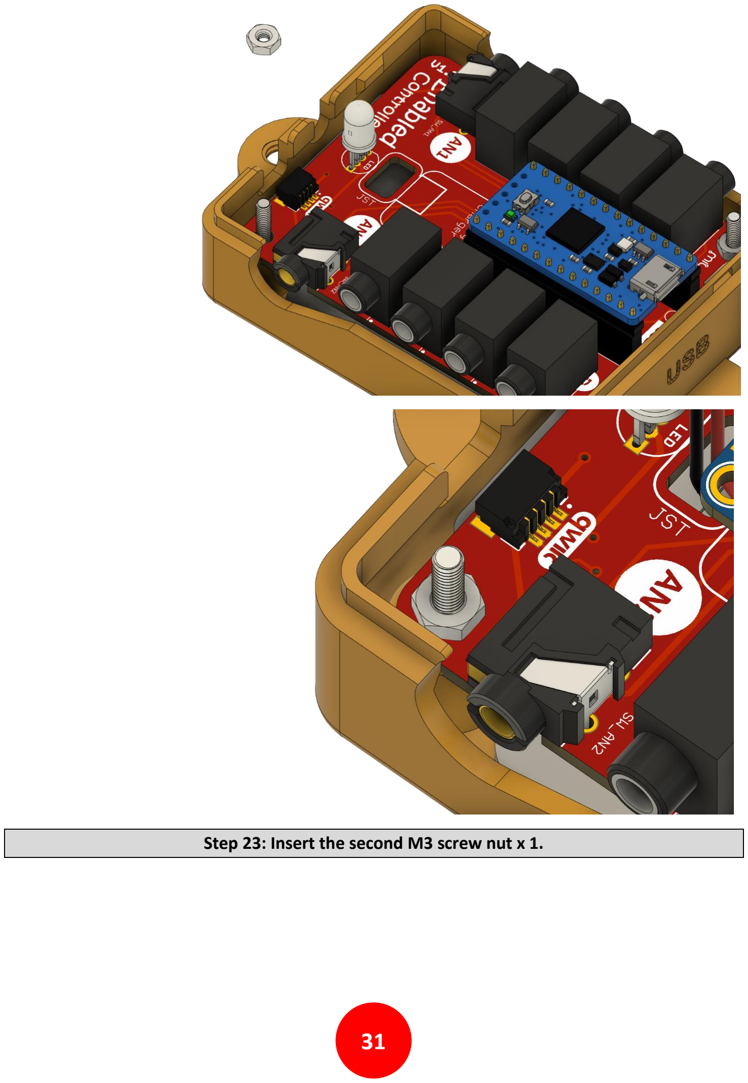
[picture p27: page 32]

31

Step 23: Insert the second M3 screw nut x 1.

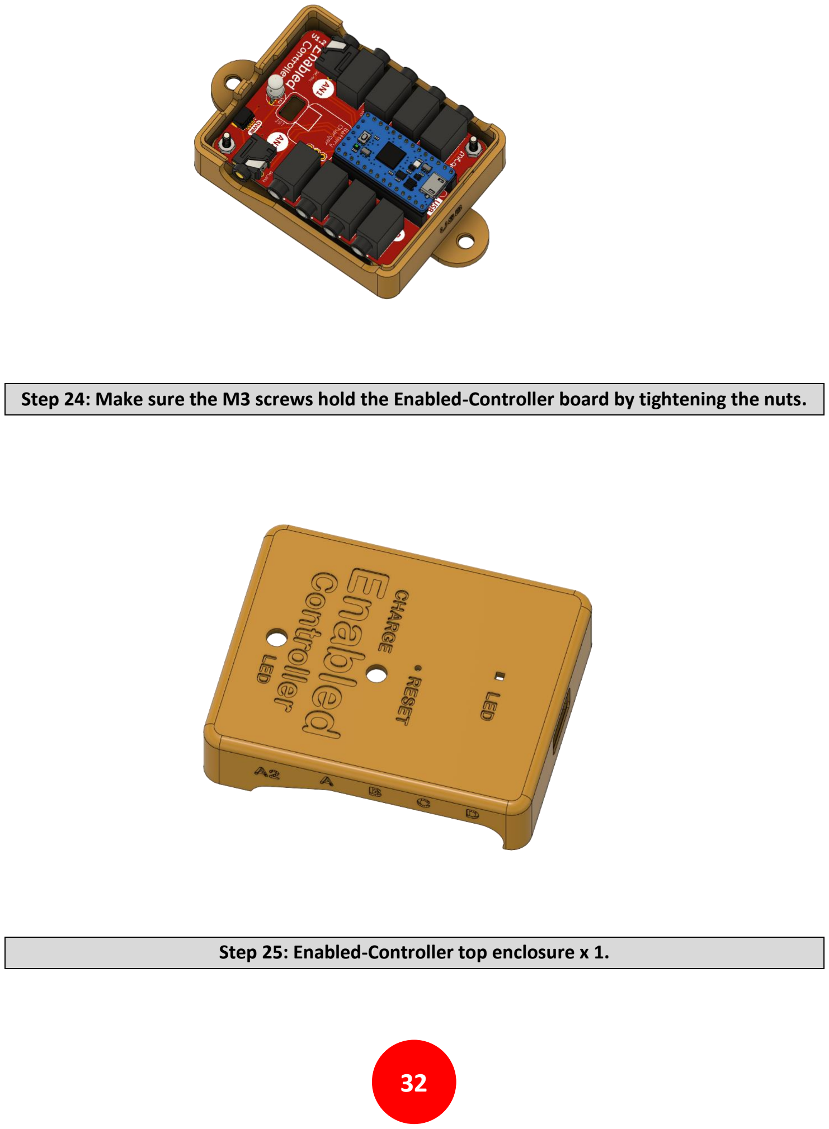
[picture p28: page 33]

32

Step 24: Make sure the M3 screws hold the Enabled-Controller board by tightening the nuts.
Step 25: Enabled-Controller top enclosure x 1.

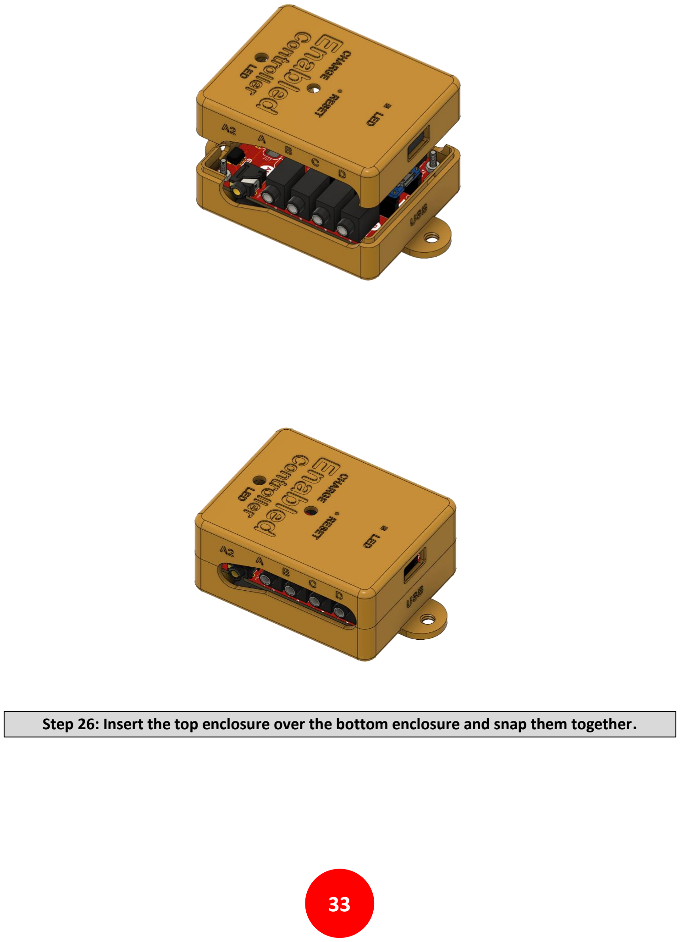
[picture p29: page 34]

33

Step 26: Insert the top enclosure over the bottom enclosure and snap them together.

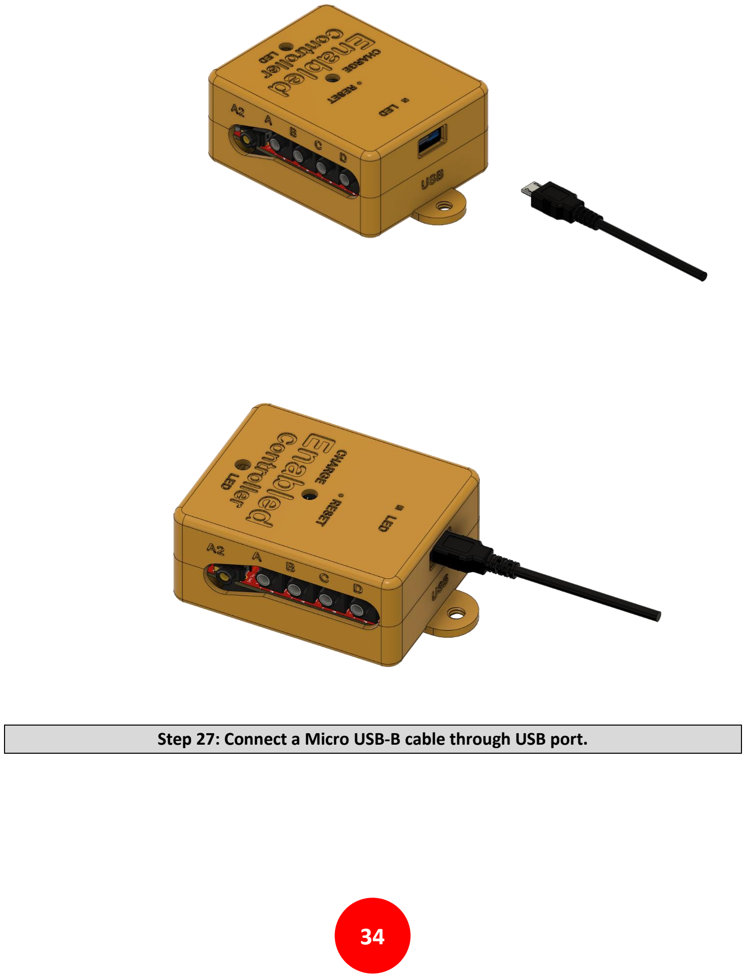
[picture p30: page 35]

34

Step 27: Connect a Micro USB-B cable through USB port.

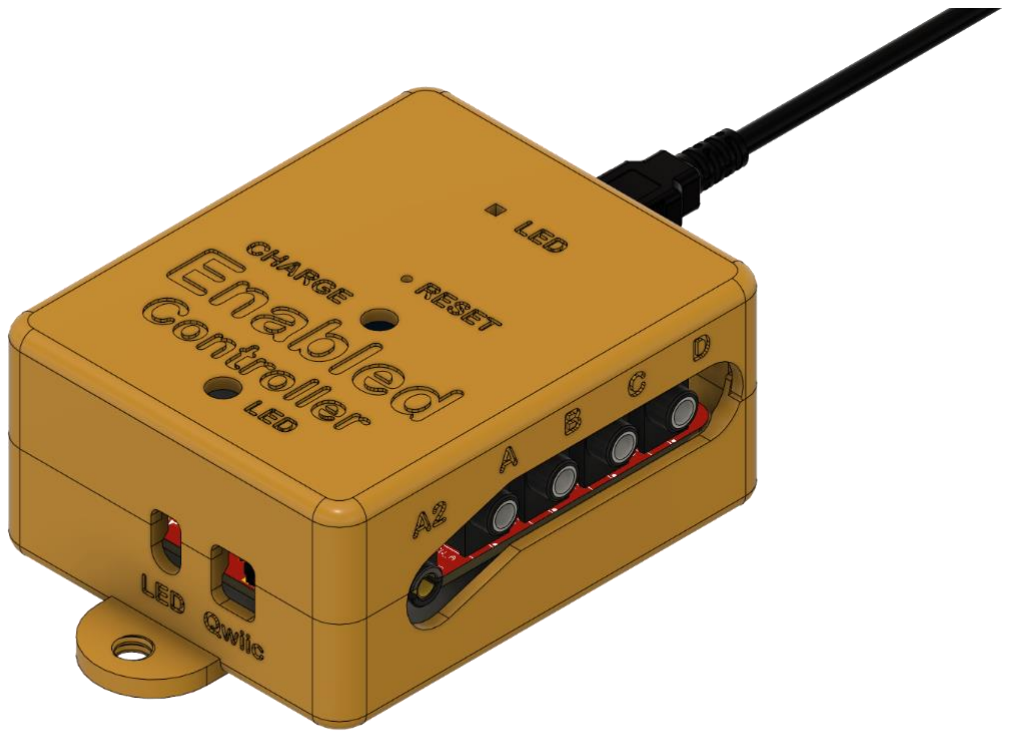
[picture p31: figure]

35

Step 28 – That’s it! Your Enabled-Controller is fully assembled and ready to use.

ready to use.

36

### Joystick Assembly

Enabled-Controller includes two 4 conductors input 3.5mm jacks reserved to connect up to two dual axis joysticks. The order of pins in joystick boards can vary depending on the brand but the following general configuration can be used to attach analog joystick. Enabled-Controller is designed to work with analog joystick which rated to work with 3.3V input voltage.

Figure 1: 4 Conductor plug (TRRS) pin mapping

The following table can summarize figure 1 as following:

PIN | FUNCTION
1 (Sleeve) | Microphone – VCC (3.3V)
2 (Ring 2) | GND
3 (Ring 1) | RT(Right Audio Channel)
4 (Tip) | LT(Left Audio Channel)
Table 1: 4 Conductor plug (TRRS) pin mapping

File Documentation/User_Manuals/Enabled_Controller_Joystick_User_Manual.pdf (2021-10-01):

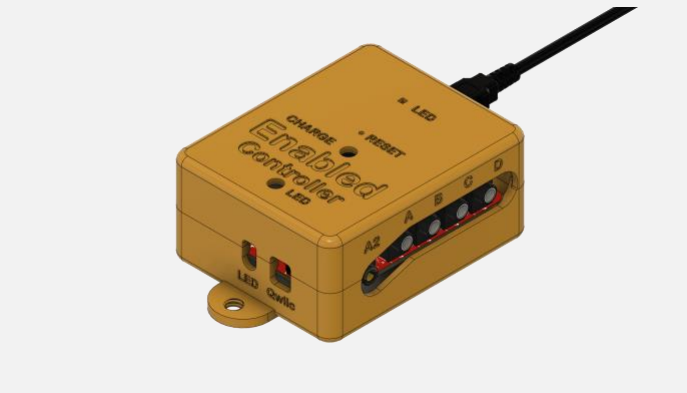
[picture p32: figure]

# ENABLED-CONTROLLER JOYSTICK USER MANUAL

An accessible adaptive switch interface box

## Version 1.2

https://github.com/milador/Enabled-Controller

1

## Contents

Usage | 2
Customization | 3

2

## Usage

The Enabled Controller Joystick can used in different configurations based on the needs of the end user. The Enabled Controller hardware can be used along different software as input device for multiple devices. The hardware allows you connect up to eight input 3.5mm adaptive switches which are marked A,B,C,D,UP,RIGHT,DOWN,LEFT on both circuit board and the enclosure.

Four switches marked as A,B,C,D can be used as input buttons when short pressed and other four switches marked as RIGHT,DOWN,LEFT are used as D-PAD directional buttons.

Table 1 represents all the possible actions for switches and their corresponding led feedback.

Button | XAC | Action | Color
A | X1 | Short press | Blue
B | X2 | Short press | Yellow
C | A | Short press | Green
D | B | Short press | Red
UP | UP D-PAD | Short press | Orange
RIGHT | RIGHT D-PAD | Short press | Orange
DOWN | DOWN D-PAD | Short press | Orange
LEFT | LEFT D-PAD | Short press | Orange
Table 1: Enabled Controller Joystick switch actions and feedback

The device will blink two times in the color of operating mode when the initialization process is completed and will stay in that color. The led will blink momentary in color of the switch pressed as represented in Table 1 and the led color will go back to the color of operating mode.

The Joystick version is great for usage along computer or for gaming purposes as it’s able to simulate an USB joystick device. The Joystick version can operate in different modes as it’s represented in Table 2.

Mode Number | Mode | Color
1 | Mode 1 | Teal
Table 2: Enabled Controller Joystick modes

The Analog AN1 and AN2 four connection input 3.5mm adaptive switches are used to connect joysticks. You can connect a dual axis joystick (X axis and Y axis) to each analog switch connection jack. By default, only AN1 is enabled.

3

### Customization

The Enabled Controller joystick can easily be customized by changing the value of variables at the beginning of Enabled Controller Joystick software. The following variables can be changed for customization purposes:

#define JOYSTICK_DEADZONE 20

The deadzone value of analog joysticks for each axis

#define JOYSTICK_NUMBER 1

The selection of active analog joystick (No Joystick = 0; A1 = 1 , A2 = 2)

#define SWITCH_REACTION_TIME 50

The switch reaction time multiplier between each switch action

#define SWITCH_MODE 1

There’s only one switch mode available

#define LED_BRIGHTNESS 100

The brightness of led for mode indication

#define LED_ACTION_BRIGHTNESS 100

The brightness of led for action indication

//Switch properties

const switchStruct switchProperty[] {

{1,"X1",1,5,5},

{2,"X2",2,6,3},

{3,"A",3,7,1},

{4,"B",4,8,6},

{5,"M",5,4} | //D-PAD Direction Buttons

};

The third column can be changed for customization of led feedback.

//Mode properties

const modeStruct modeProperty[] {

{1,"Mode 1",8}

};

The third column can be changed for customization of led feedback.

4

const colorStruct colorProperty[] {

{1,"Green",{0,50,0}},

{2,"Pink",{50,00,20}},

{3,"Yellow",{50,50,0}},

{4,"Orange",{50,20,0}},

{5,"Blue",{0,0,50}},

{6,"Red",{50,0,0}},

{7,"Purple",{50,0,50}},

{8,"Teal",{0,128,128}}

};

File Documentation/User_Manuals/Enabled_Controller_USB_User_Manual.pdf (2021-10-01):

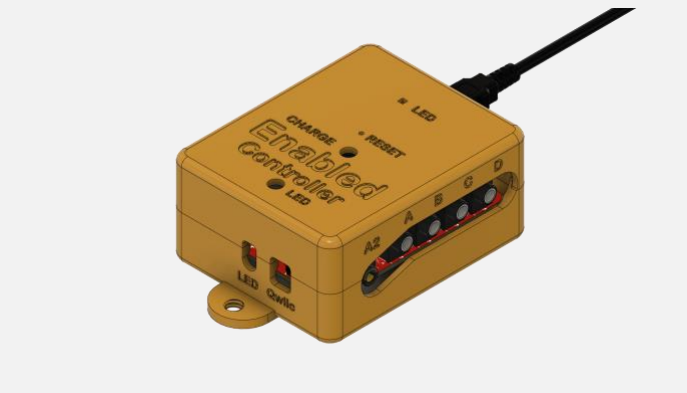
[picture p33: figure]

# ENABLED CONTROLLER USB USER MANUAL

An accessible adaptive switch interface box

## Version 1.2

https://github.com/milador/Enabled-Controller

1

## Contents

Usage | 2
Keyboard Switch mode | 2
Morse Keyboard Mode | 4
Morse Mouse Mode | 4
Mouse Mode | 5
Settings Mode | 6
Customization | 6

2

## Usage

The Enabled Controller USB can be used in different configurations based on the needs of the end user. The Enabled Controller hardware can be used along different software as input device for multiple devices. The hardware allows you connect up to eight input 3.5mm adaptive switches which are marked A,B,C,D,UP,RIGHT,DOWN,LEFT on both circuit board and the enclosure.

All four switches can be used as inputs when short pressed and switch D can be used to change the operation mode when it’s pressed and hold for more than 2 seconds. Table 1 represents all the possible actions for switches and their corresponding led feedback.

Button | Action | Color
A | Short press | Blue
B | Short press | Red
C | Short press | Green
D | Short press | Yellow
D | Long Press | Mode Led Color
UP | Short press | Yellow
RIGHT | Short press | Yellow
DOWN | Short press | Yellow
LEFT | Short press | Yellow
Table 1: Enabled Controller USB switch actions and feedback

The device will blink two times in the color of operating mode when the initialization process is completed and will stay in that color. The led will blink momentary in color of the switch pressed as represented in Table 1 and the led color will go back to the color of operating mode. The mode can only change when switch D is pressed and hold for 2 seconds.

The USB version is great for usage along computer or smartphone devices as it’s able to simulate a USB mouse or USB keyboard device. The USB version can operate in different modes as it’s represented in Table 2.

Mode Number | Mode | Color
1 | Keyboard Switch | Teal
2 | Morse Keyboard | Purple
3 | Morse Mouse | Pink
4 | Mouse | Green
5 | Settings | Orange
Table 2: Enabled Controller USB modes

Keyboard Switch mode
The Keyboard Switch will operate similar to a four key keyboard which is great for using as switches for your computer or smartphone device through features such as Switch access and it can also be used to play computer games via WASD format keyboard.

The switch mode does not work the exact same way in all the Operating Systems and as the results, you may need to modify the keystrokes sent for each switch.

3

Enabled-Controller has two OS profile options which you can select from depending on the Operating System of your host device.

OS PROFILE #1: Windows and Android

Button | Action | Color | Result
A | Short press | Blue | Send ‘a’ keystroke
B | Short press | Red | Send ‘b’ keystroke
C | Short press | Green | Send ‘c’ keystroke
D | Short press | Yellow | Send ‘d’ keystroke
D | Long Press | Mode Led Color | Change operating mode
UP | Short press | Yellow | Send KEY_UP_ARROW keystroke
RIGHT | Short press | Yellow | Send KEY_RIGHT_ARROW keystroke
DOWN | Short press | Yellow | Send KEY_DOWN_ARROW keystroke
LEFT | Short press | Yellow | Send KEY_LEFT_ARROW keystroke
Table 3: Enabled Controller USB switch actions (OS PROFILE #1)

OS PROFILE #2: macOS

Button | Action | Color | Result
A | Short press | Blue | Send KEY_F1 keystroke
B | Short press | Red | Send KEY_F2 keystroke
C | Short press | Green | Send KEY_F3 keystroke
D | Short press | Yellow | Send KEY_F4 keystroke
D | Long Press | Mode Led Color | Change operating mode
UP | Short press | Yellow | Send KEY_F5 keystroke
RIGHT | Short press | Yellow | Send KEY_F6 keystroke
DOWN | Short press | Yellow | Send KEY_F7 keystroke
LEFT | Short press | Yellow | Send KEY_F8 keystroke
Table 4: Enabled Controller USB switch actions (OS PROFILE #2)

The time between each switch press actions is calculated by switch reaction levels which can be changed in settings mode or manually through the software. The switch reaction time variable is used to calculate the reaction time for each of the 10 levels as represented in Table 5.

SWITCH_REACTION_TIME 50

The switch reaction time variable is set to 50 by default.

Level | 10 | 9 | 8 | 7 | 6 | 5 | 4 | 3 | 2 | 1
Time (ms) | 1*50 | 2*50 | 3*50 | 4*50 | 5*50 | 6*50 | 7*50 | 8*50 | 9*50 | 10*50

Table 5: Enabled Controller USB switch reaction time

4

Morse Keyboard Mode
This mode is used to convert morse code to keystrokes via 2 switches. The first switch acts as dot and second switch acts as dash as explained in Table 6.
Button | Action | Color | Result
A | Short press | Blue | Send ‘.’ To morse stack
B | Short press | Red | Send ‘-’ To morse stack
D | Long Press | Mode Led Color | Change operating mode
Table 6: Enabled Controller USB morse keyboard mode

The conversion of morse code combination to characters is done in software based on the static variables in the beginning of the code. These values can be customized based on your needs.

MORSE_TIMEOUT 1000

MORSE_REACTION_TIME 10

The timeout is the time in ms that is measured since last switch action to perform the morse conversation and send the result as keystroke. The time by default is set to 1 second ( 1000 ms ) which means the device will convert the morse code combinations if switch A and B (Dot , Dash ) are not pressed for 1 second.

The reaction time is the multiplier for time between each dot and dash. The higher reaction level means lower reaction time. The reaction levels can be changed using switches in the settings mode but it’s also possible to change the morse reaction time multiplier in the code. Table 7 can be used to understand the morse reaction time calculation.

Lev el | 10 | 9 | 8 | 7 | 6 | 5 | 4 | 3 | 2 | 1
Time (ms) | (1.5^1)* 10 | (1.5^2)* 10 | (1.5^3)* 10 | (1.5^4)* 10 | (1.5^5)* 10 | (1.5^6)* 10 | (1.5^7)* 10 | (1.5^8)* 10 | (1.5^9)* 10 | (1.5^10)* 10

Table 7: Enabled Controller USB morse reaction time

The table of morse code combinations can be found on EasyMorse (https://github.com/milador/EasyMorse) project github repository.

Morse Mouse Mode
This mode is used to convert morse code to mouse actions via 2 switches. The first switch acts as dot and second switch acts as dash as explained in Table 8.
Button | Action | Color | Result
A | Short press | Blue | Send ‘.’ To morse stack
B | Short press | Red | Send ‘-’ To morse stack
D | Long Press | Mode Led Color | Change operating mode
Table 8: Enabled Controller USB morse mouse mode

This mode users the morse timeout value and morse reaction time to convert morse code combinations to mouse actions similar to morse keyboard mode. The table of morse code combinations can be found on EasyMorse (https://github.com/milador/EasyMorse) project github repository. The conversion table is represented in Table 9 in addition.

5

Morse code | Result
- Move Up
-- | Move Down
.. | Move Left
... | Move Right
.- | Left Click
.-- | Right Click
..- | Double Left Click
..-- | Double Right Click
-. | Left Click & Hold/Release
-.. | Right Click & Hold/Release
Table 9: Enabled Controller USB morse mouse code conversion table

The mouse move actions are fixed in terms of number of pixels that cursor can be moved for each morse code combination, but there is mouse move multiplier variable available in the software that allows you to customize the mouse move behavior based on your needs.

MOUSE_MOVE_MULTI 2

The mouse move multiplier variable is set to 2 by default.

Mouse Mode
This mode is used to simulate a mouse device using the dual analog joysticks and input switches.
Button | Action | Color | Result
A | Short press | Blue | Left Click
B | Short press | Red | Right Click
C | Short press | Green | No Action
D | Short press | Yellow | No Action
D | Long Press | Mode Led Color | Change operating mode
Up | Short press | Yellow | No Action
Right | Short press | Yellow | No Action
Down | Short press | Yellow | No Action
Left | Short press | Yellow | No Action
Table 10: Enabled Controller USB mouse mode switch actions
Action | Color | Result
Joystick X1 | Yellow | Move Cursor Left or Right
Joystick Y1 | Yellow | Move Cursor Up or Down
Joystick X2 | Yellow | Move Cursor Left or Right
Joystick Y2 | Yellow | Move Cursor Up or Down
Table 11: Enabled Controller USB mouse mode joystick actions

6

The user has option to enable and select the analog joystick port number using constants defined in the firmware.

JOYSTICK_ENABLED false

JOYSTICK_NUMBER 2

There is an option to select the desired dead zone value based on the user ability and needs.

JOYSTICK_DEADZONE 20

Settings Mode
The settings mode is used to change the reaction level and reaction time using the A and B switches. The led will blink in blue when react level is increased and in red when reaction level is decreased. The number of led blinks indicate new reaction level. The led will blink 10 times when it reaches maximum or minimum reaction levels.
Button | Action | Color | Result
A | Short press | Blue | Increase Reaction level (Decrease Reaction time)
B | Short press | Red | Decrease Reaction level (Increase Reaction time)
D | Long Press | Mode Led Color | Change operating mode
Table 12: Enabled Controller USB settings mode

There are total of 10 levels and the switch reaction times and morse reaction times can be calculated using Tablets 11 and 12.

Level | 10 | 9 | 8 | 7 | 6 | 5 | 4 | 3 | 2 | 1
Time (ms) | 1*50 | 2*50 | 3*50 | 4*50 | 5*50 | 6*50 | 7*50 | 8*50 | 9*50 | 10*50

Table 13: Enabled Controller USB switch reaction time

Lev el | 10 | 9 | 8 | 7 | 6 | 5 | 4 | 3 | 2 | 1
Time (ms) | (1.5^1)* 10 | (1.5^2)* 10 | (1.5^3)* 10 | (1.5^4)* 10 | (1.5^5)* 10 | (1.5^6)* 10 | (1.5^7)* 10 | (1.5^8)* 10 | (1.5^9)* 10 | (1.5^10)* 10

Table 14: Enabled Controller USB morse reaction time

### Customization

The Enabled Controller USB can easily be customized by changing the value of variables at the beginning of Enabled Controller USB software. The following variables can be changed for customization purposes:

#define SWITCH_MAC_PROFILE false

This variable is created to set the keys to be used as switches based on host device OS profile (Windows & Android = false , macOS = true )

#define MORSE_TIMEOUT 1000

The time of no activity which is used as flag to convert the morse combination to keystroke

7

#define MORSE_REACTION_TIME 10

The morse reaction time multiplier between each dot and dash actions

#define MOUSE_MOVE_MULTI 2

The morse mouse move multiplier variable

#define SWITCH_REACTION_TIME 50

The switch reaction time multiplier between each switch action

#define SWITCH_MODE_CHANGE_TIME 2000

The time that switch D needs to be hold in ms to perform mode change action

#define LED_BRIGHTNESS 150

The brightness of led for mode indication

#define LED_ACTION_BRIGHTNESS 150

The brightness of led for action indication

//Switch properties

const switchStruct switchProperty[] {

{1,"DOT",HID_KEY_A,HID_KEY_F1,MOUSE_LEFT_CLICK,5,1}, //{1=dot,"DOT",'a','F1',5=blue,1=1xMORSE_REACTION}

{2,"DASH",HID_KEY_B,HID_KEY_F2,MOUSE_RIGHT_CLICK,6,3}, //{2=dash,"DASH",'b','F2',6=red,3=3xMORSE_REACTION}

{3,"C",HID_KEY_C,HID_KEY_F3,MOUSE_DOUBLE_LEFT_CLICK,1,1}, //{3,"C",'c','F3',1=green,1=1xMORSE_REACTION}

{4,"D",HID_KEY_D,HID_KEY_F4,MOUSE_DOUBLE_RIGHT_CLICK,3,1}, //{4,"D",'d','F4',3=yellow,1=1xMORSE_REACTION}

{5,"UP",HID_KEY_ARROW_UP,HID_KEY_F5,MOUSE_NO_ACTION,4,1}, //{5,"UP",'UP','F5',4=orange,1=1xMORSE_REACTION}

{6,"RIGHT",HID_KEY_ARROW_RIGHT,HID_KEY_F6,MOUSE_NO_ACTION,4,1}, //{6,"RIGHT",'RIGHT','F6',4=orange,1=1xMORSE_REACTION}

{7,"DOWN",HID_KEY_ARROW_DOWN,HID_KEY_F7,MOUSE_NO_ACTION,4,1}, //{7,"DOWN",'DOWN','F7',4=orange,1=1xMORSE_REACTION}

{8,"LEFT",HID_KEY_ARROW_LEFT,HID_KEY_F8,MOUSE_NO_ACTION,4,1}, //{8,"LEFT",'LEFT','F8',4=orange,1=1xMORSE_REACTION}

{9,"ANALOG",HID_KEY_NONE,HID_KEY_NONE,MOUSE_NO_ACTION,4,1} //{9,"ANALOG",'NONE','F9',4=orange,1=1xMORSE_REACTION}};

8

The values of third column can be changed to different characters and the fourth column can be changed for customization of led feedback.

//Settings Action properties

const settingsActionStruct settingsProperty[] {

{1,"Increase Reaction",5}, | //{1=Increase Reaction,5=blue}
{2,"Decrease Reaction",6}, | //{2=Decrease Reaction,6=red}
{3,"Max Reaction",1}, | //{3=Max Reaction,1=green}
{4,"Min Reaction",1} | //{4=Min Reaction,1=green}

};

The third column can be changed for customization of led feedback.

//Mode properties

const modeStruct modeProperty[] {

{1,"Keyboard Switch",8},

{2,"Morse Keyboard",7},

{3,"Morse Mouse",2},

{4,"Mouse",1},

{5,"Settings",4}

};

The third column can be changed for customization of led feedback.

const colorStruct colorProperty[] {

{1,"Green",{0,50,0}},

{2,"Pink",{50,00,20}},

{3,"Yellow",{50,50,0}},

{4,"Orange",{50,20,0}},

{5,"Blue",{0,0,50}},

{6,"Red",{50,0,0}},

{7,"Purple",{50,0,50}},

{8,"Teal",{0,128,128}}

};

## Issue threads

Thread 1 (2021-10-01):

### ISSUE TITLE
Suggestion: screw sizing

### ISSUE THREAD

**Issue by scruss** [milador/Enabled-Controller#1]
Hey, lovely project here!

One (very) minor thing: there's no explicit length on the BOM for the 6-32 screw. I can see from the Digikey part link it's ½", but nothing on the documentation.

Also, could an M3 by 12 mm cross head screw be substituted? I couldn't quite work out if it would be quite long enough. 6-32 screws aren't easily available outside North America, and slot-head screw drivers are classed as bladed tools, so aren't permitted in schools in some countries.

**Comment by milador** [comment]
Good point there. M3 by 6 mm should work but I haven’t got chance to try different options. Had these around so used them. I update the link once I try it. Great feedback as usual. Made the mini version with Adafruit QT PY as well.

**Comment by milador** [comment]
@scruss Changed the screws to M3 and they work well. Thanks for your excellent feedback.

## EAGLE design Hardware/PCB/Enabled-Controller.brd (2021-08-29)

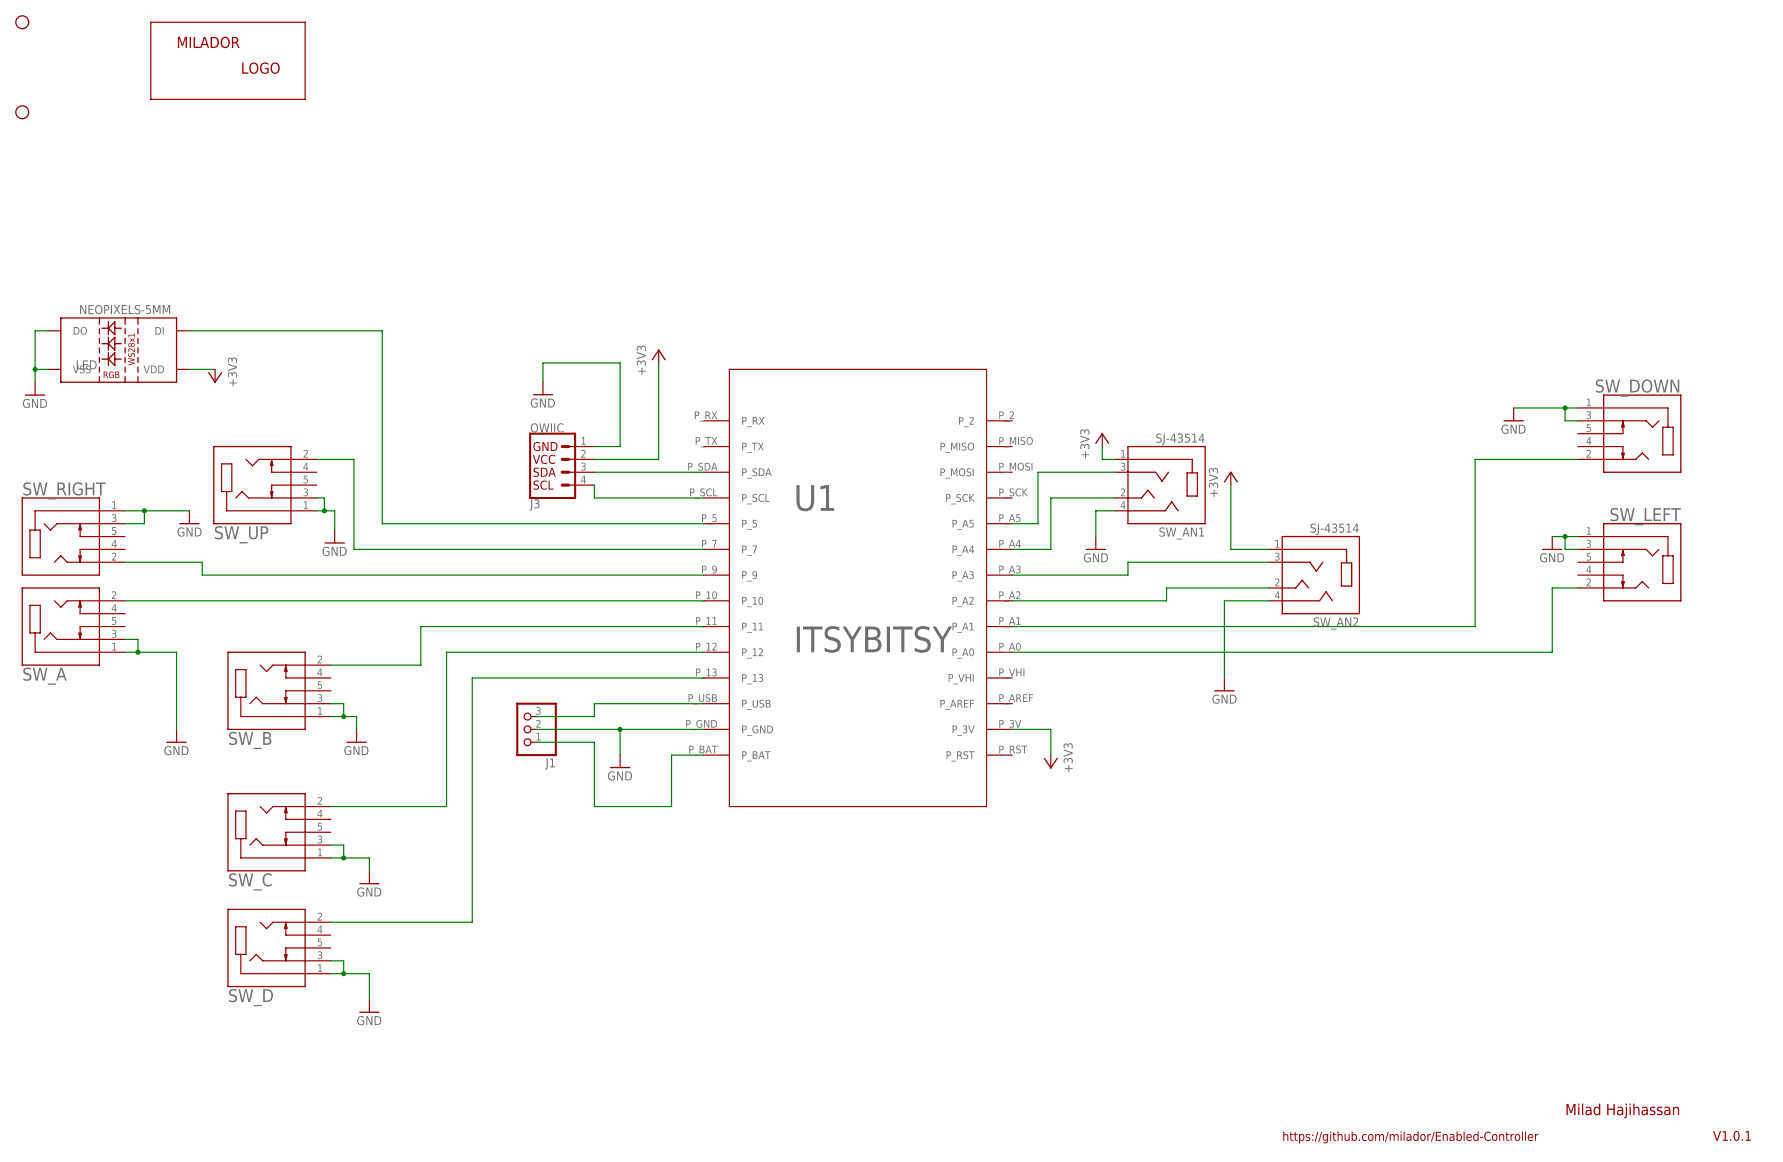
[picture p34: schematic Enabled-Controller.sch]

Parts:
J1: HEADER_FEMALE-1X3-LONGER; HEADER_FEMALE-1X03_LONGER
J3: QWIIC; CONNECTORS_JST04_1MM_RA
LABEL1: MILADOR-LOGO-; MILADOR_LOGO1
LED: NEOPIXELS-5MM
STANDOFF1, STANDOFF2: STAND-OFF-; STAND-OFF
SW_A: CUI_SJ1-3535NGSJ1-3535NG; CUI_SJ1-3535NG
SW_AN1, SW_AN2: SJ-43514; CUI_SJ-43514
SW_B: CUI_SJ1-3535NGSJ1-3535NG; CUI_SJ1-3535NG
SW_C: CUI_SJ1-3535NGSJ1-3535NG; CUI_SJ1-3535NG
SW_D: CUI_SJ1-3535NGSJ1-3535NG; CUI_SJ1-3535NG
SW_DOWN: CUI_SJ1-3535NGSJ1-3535NG; CUI_SJ1-3535NG
SW_LEFT: CUI_SJ1-3535NGSJ1-3535NG; CUI_SJ1-3535NG
SW_RIGHT: CUI_SJ1-3535NGSJ1-3535NG; CUI_SJ1-3535NG
SW_UP: CUI_SJ1-3535NGSJ1-3535NG; CUI_SJ1-3535NG
U1: ITSYBITSY; ITSYBITSY-V2

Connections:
+3V3: J3.2, LED.P2 (VDD), SW_AN1.1 (SLEEVE), SW_AN2.1 (SLEEVE), U1.P_3V
GND: J1.2, J3.1, LED.P3 (VSS), LED.P4 (DO), SW_A.1, SW_A.3, SW_AN1.4 (RING2), SW_AN2.4 (RING2), SW_B.1, SW_B.3, SW_C.1, SW_C.3, SW_D.1, SW_D.3, SW_DOWN.1, SW_DOWN.3, SW_LEFT.1, SW_LEFT.3, SW_RIGHT.1, SW_RIGHT.3, SW_UP.1, SW_UP.3, U1.P_GND
unnamed: SW_D.2, U1.P_13
unnamed: SW_C.2, U1.P_12
unnamed: SW_B.2, U1.P_11
unnamed: SW_AN1.2 (TIP), U1.P_A4
unnamed: SW_DOWN.2, U1.P_A1
unnamed: SW_RIGHT.2, U1.P_9
unnamed: SW_UP.2, U1.P_7
unnamed: SW_AN1.3 (RING1), U1.P_A5
unnamed: SW_AN2.3 (RING1), U1.P_A3
unnamed: SW_A.2, U1.P_10
unnamed: SW_LEFT.2, U1.P_A0
unnamed: SW_AN2.2 (TIP), U1.P_A2
unnamed: LED.P1 (DI), U1.P_5
unnamed: J3.4, U1.P_SCL
unnamed: J3.3, U1.P_SDA
unnamed: J1.3, U1.P_USB
unnamed: J1.1, U1.P_BAT

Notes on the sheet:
V1.0.1
Milad Hajihassan
https://github.com/milador/Enabled-Controller

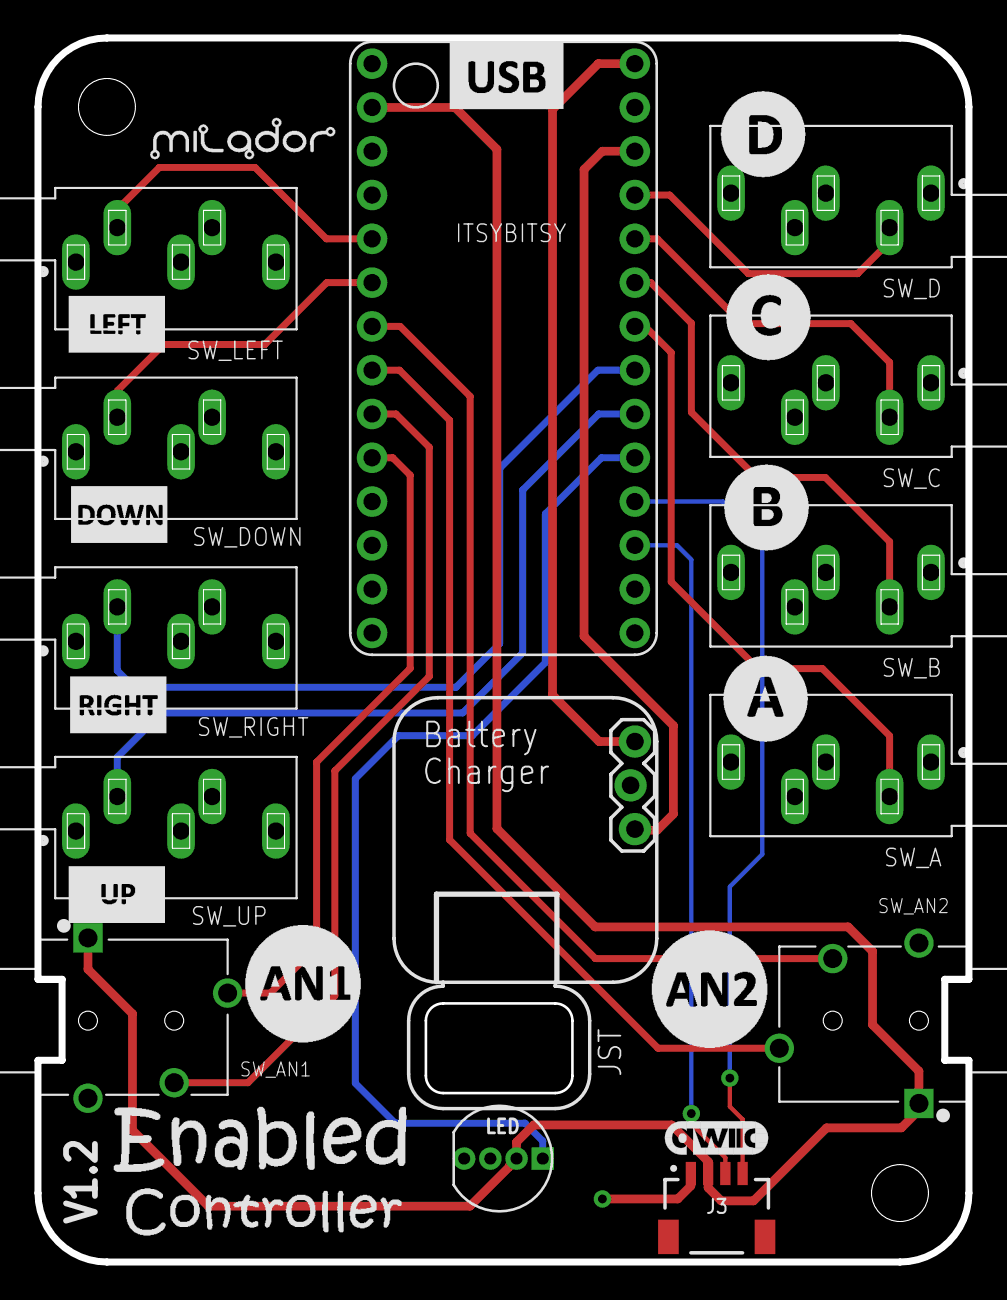
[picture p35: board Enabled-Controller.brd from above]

Board: 2 copper layers, 54.0 x 71.0 mm, 18 parts (0 on the bottom side), 19 nets.

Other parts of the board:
LABEL2: QWIIC_6MM

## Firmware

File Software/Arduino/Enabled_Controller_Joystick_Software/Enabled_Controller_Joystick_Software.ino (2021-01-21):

/***************************************************************************
 * File Name: Enabled_Controller_Joystick_Software.ino 
 * Title: Enabled Controller Mini Joystick Software
 * Developed by: Milad Hajihassan
 * Version Number: 1.0 (20/1/2021)
 * Github Link: https://github.com/milador/Enabled_Controller
 ***************************************************************************/

#include "Joystick.h"
#include <math.h>
#include <Adafruit_NeoPixel.h>
#include <Adafruit_DotStar.h>


//Can be changed based on the needs of the users 
#define JOYSTICK_DEADZONE 20                                          //Joystick deadzone
#define JOYSTICK_NUMBER 2                                             //No Joystick = 0; A1 = 1 , A2 = 2 
#define SWITCH_REACTION_TIME 50                                       //Minimum time for each switch action
#define SWITCH_MODE 1                                                 //Only one mode


#define LED_BRIGHTNESS 100                                             //The mode led color brightness which is always on ( Use a low value to decrease power usage )
#define LED_ACTION_BRIGHTNESS 100                                      //The action led color brightness which can be a higher value than LED_BRIGHTNESS


//Define Switch pins
#define LED_PIN 5
#define DOTSTAR_DATA_PIN    41
#define DOTSTAR_CLOCK_PIN   40


#define SWITCH_A_PIN 10
#define SWITCH_B_PIN 11
#define SWITCH_C_PIN 12
#define SWITCH_D_PIN 13

#define SWITCH_UP_PIN 7
#define SWITCH_RIGHT_PIN 9
#define SWITCH_DOWN_PIN A1
#define SWITCH_LEFT_PIN A0

//Define Joystick pins
#define JOYSTICK_X1_PIN A4
#define JOYSTICK_Y1_PIN A5  
#define JOYSTICK_X2_PIN A2
#define JOYSTICK_Y2_PIN A3  

// Variable Declaration

//Declare switch state variables for each switch
int switchAState;
int switchBState;
int switchCState;
int switchDState;

int switchUpState;
int switchRightState;
int switchDownState;
int switchLeftState;

//Previous status of switches
int switchAPrevState = HIGH;          
int switchBPrevState = HIGH;
int switchCPrevState = HIGH;
int switchDPrevState = HIGH;

int switchUpPrevState = HIGH;          
int switchRightPrevState = HIGH;
int switchDownPrevState = HIGH;
int switchLeftPrevState = HIGH;

//Declare joystick variables 
int joystickX;
int joystickY;


//Declare Switch variables for settings 
int switchConfigured;
int switchReactionTime;
int switchReactionLevel;
int switchMode;


//RGB LED Color code structure 

struct rgbColorCode {
    int r;    // red value 0 to 255
    int g;   // green value
    int b;   // blue value
 };

//Color structure 
typedef struct { 
  uint8_t colorNumber;
  String colorName;
  rgbColorCode colorCode;
} colorStruct;

 //Mode structure 
typedef struct { 
  uint8_t modeNumber;
  String modeName;
  uint8_t modeColorNumber;
} modeStruct;


 //Switch structure 
typedef struct { 
  uint8_t switchNumber;
  String switchButtonName;
  uint8_t switchModeButtonNumber;
  uint8_t switchColorNumber;
} switchStruct;


 //Settings Action structure 
typedef struct { 
  uint8_t settingsActionNumber;
  String settingsActionName;
  uint8_t settingsActionColorNumber;
} settingsActionStruct;

//Color properties 
const colorStruct colorProperty[] {
    {1,"Green",{0,50,0}},
    {2,"Pink",{50,00,20}},
    {3,"Yellow",{50,50,0}},    
    {4,"Orange",{50,20,0}},
    {5,"Blue",{0,0,50}},
    {6,"Red",{50,0,0}},
    {7,"Purple",{50,0,50}},
    {8,"Teal",{0,128,128}}       
};

//Switch properties 
const switchStruct switchProperty[] {
    {1,"A",1,5},
    {2,"B",2,3},
    {3,"C",3,1},
    {4,"D",4,6},
    {5,"M",5,4}
    
};

//Mode properties 
const modeStruct modeProperty[] {
    {1,"Mode 1",8}
};


//Setup NeoPixel LED
Adafruit_NeoPixel ledPixels = Adafruit_NeoPixel(1, LED_PIN, NEO_GRB + NEO_KHZ800);
Adafruit_DotStar dotStar(1, DOTSTAR_DATA_PIN, DOTSTAR_CLOCK_PIN, DOTSTAR_BRG);

//Defining the joystick REPORT_ID and profile type
Joystick_ Joystick(JOYSTICK_DEFAULT_REPORT_ID, 
  JOYSTICK_TYPE_JOYSTICK, 8, 0,
  true, true, false, 
  false, false, false,
  false, false, 
  false, false, false);   

void setup() {

  ledPixels.begin();                                                           //Start NeoPixel
  Serial.begin(115200);                                                        //Start Serial
  switchSetup();
  delay(5);
  joystickSetup();
  delay(1000);
  initLedFeedback();                                                          //Led will blink in a color to show the current mode 
  delay(5);
  displayFeatureList();
  
  //Initialize the switch pins as inputs
  pinMode(SWITCH_A_PIN, INPUT_PULLUP);    
  pinMode(SWITCH_B_PIN, INPUT_PULLUP);   
  pinMode(SWITCH_C_PIN, INPUT_PULLUP);    
  pinMode(SWITCH_D_PIN, INPUT_PULLUP);  
  
  pinMode(SWITCH_UP_PIN, INPUT_PULLUP);    
  pinMode(SWITCH_RIGHT_PIN, INPUT_PULLUP);   
  pinMode(SWITCH_DOWN_PIN, INPUT_PULLUP);    
  pinMode(SWITCH_LEFT_PIN, INPUT_PULLUP);

  //Initialize the LED pin as an output
  pinMode(LED_PIN, OUTPUT);                                                      


};

void loop() {
  //Perform joystick actions based on the mode
  joystickAction(switchMode);
  dotStar.show(); 
  ledPixels.show(); 
  delay(5);
}

//***DISPLAY FEATURE LIST FUNCTION***//

void displayFeatureList(void) {

  Serial.println(" ");
  Serial.println(" --- ");
  Serial.println("This is the Enabled Controller USB Software");
  Serial.println(" ");
  Serial.println("VERSION: 1.1 (20 January 2021)");
  Serial.println(" ");
  Serial.println(" --- ");
  Serial.println("Features: Joystick ");
  Serial.println(" --- ");
  Serial.println(" ");

}

//***RGB LED FUNCTION***//

void setLedBlink(int numBlinks, int delayBlinks, int ledColor,uint8_t ledBrightness) {
  if (numBlinks < 0) numBlinks *= -1;

      for (int i = 0; i < numBlinks; i++) {
        dotStar.setPixelColor(0, dotStar.Color(colorProperty[ledColor-1].colorCode.g,colorProperty[ledColor-1].colorCode.r,colorProperty[ledColor-1].colorCode.b));
        dotStar.setBrightness(ledBrightness);
        dotStar.show(); 
        ledPixels.setPixelColor(0, ledPixels.Color(colorProperty[ledColor-1].colorCode.g,colorProperty[ledColor-1].colorCode.r,colorProperty[ledColor-1].colorCode.b));
        ledPixels.setBrightness(ledBrightness);
        ledPixels.show(); 
        delay(delayBlinks);
        dotStar.setPixelColor(0, dotStar.Color(0,0,0));
        ledPixels.setBrightness(ledBrightness);
        dotStar.show();   
        ledPixels.setPixelColor(0, ledPixels.Color(0,0,0));
        ledPixels.setBrightness(ledBrightness);
        ledPixels.show(); 
        delay(delayBlinks);
      }
}

//***UPDATE RGB LED COLOR FUNCTION***//

void updateLedColor(int ledColor, uint8_t ledBrightness) {
    dotStar.setPixelColor(0, dotStar.Color(colorProperty[ledColor-1].colorCode.g,colorProperty[ledColor-1].colorCode.r,colorProperty[ledColor-1].colorCode.b));
    dotStar.setBrightness(ledBrightness);
    dotStar.show();
    ledPixels.setPixelColor(0, ledPixels.Color(colorProperty[ledColor-1].colorCode.g,colorProperty[ledColor-1].colorCode.r,colorProperty[ledColor-1].colorCode.b));
    ledPixels.setBrightness(ledBrightness);
    ledPixels.show();
}

//***GET RGB LED COLOR FUNCTION***//

uint32_t getLedColor(int ledModeNumber) {

  int colorNumber= modeProperty[ledModeNumber-1].modeColorNumber-1;
  
  //return (dotStar.Color(colorProperty[colorNumber].colorCode.g,colorProperty[colorNumber].colorCode.r,colorProperty[colorNumber].colorCode.b));
  return (ledPixels.Color(colorProperty[colorNumber].colorCode.g,colorProperty[colorNumber].colorCode.r,colorProperty[colorNumber].colorCode.b));
}

//***GET RGB LED BRIGHTNESS FUNCTION***//

uint8_t getLedBrightness() {
  return (ledPixels.getBrightness());
}

//***SET RGB LED COLOR FUNCTION***//

void setLedColor (uint32_t ledColor, uint8_t ledBrightness){
  dotStar.setPixelColor(0, ledColor);
  dotStar.setBrightness(ledBrightness);
  dotStar.show(); 
    
  ledPixels.setPixelColor(0, ledColor);
  ledPixels.setBrightness(ledBrightness);
  ledPixels.show(); 

}

//***SET RGB LED BRIGHTNESS FUNCTION***//

void setLedBrightness(uint8_t ledBrightness) {
  ledPixels.setBrightness(ledBrightness);
  ledPixels.show();
}

//***CLEAR RGB LED FUNCTION***//

void ledClear() {
  dotStar.setPixelColor(0, dotStar.Color(0,0,0));
  dotStar.show(); 
  ledPixels.setPixelColor(0, ledPixels.Color(0,0,0));
  ledPixels.show(); 
}

//***SWITCH FEEDBACK FUNCTION***//

void switchFeedback(int switchNumber,int modeNumber,int delayTime, int blinkNumber =1)
{
  //Get previous led color and brightness 
  uint32_t previousColor = getLedColor(modeNumber);
  uint8_t previousBrightness = getLedBrightness();
 
  setLedBlink(blinkNumber,delayTime,switchProperty[switchNumber-1].switchColorNumber,LED_ACTION_BRIGHTNESS);
  delay(5);

  //Set previous led color and brightness 
  setLedColor(previousColor,previousBrightness);
  
}

//***MODE FEEDBACK FUNCTION***//

void modeFeedback(int modeNumber,int delayTime, int blinkNumber =1)
{

   //Get new led color and brightness 
  uint32_t newColor = getLedColor(modeNumber);
  uint8_t newBrightness = getLedBrightness();
  
  setLedBlink(blinkNumber,delayTime,modeProperty[modeNumber-1].modeColorNumber,LED_ACTION_BRIGHTNESS);
  delay(5);

  //Set new led color and brightness 
  setLedColor(newColor,newBrightness);
  
}


//***SETUP SWITCH HID PROFILES FUNCTION (LOAD HID PROFILES)***//

void joystickSetup(){
      //Setup joystick library 
      Joystick.begin(); 

      //Set joystick x,y range
      Joystick.setXAxisRange(-127, 127);
      Joystick.setYAxisRange(-127, 127);

}

//***PERFORM JOYSTICK ACTIONS FUNCTION***//
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

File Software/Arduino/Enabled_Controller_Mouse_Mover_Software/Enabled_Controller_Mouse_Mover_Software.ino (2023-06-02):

/** ************************************************************************
 * File Name: Enabled_Controller_Mouse_Mover_Software.ino 
 * Title: Enabled Controller Mouse Mover Software
 * Developed by: Milad Hajihassan
 * Version Number: 1.2 (06/5/2023)
 * Github Link: https://github.com/milador/Enabled_Controller
 ***************************************************************************/

#include "Mouse.h"
#include <StopWatch.h>
#include <math.h>
#include <Adafruit_NeoPixel.h>
#include <Adafruit_DotStar.h>
#include <FlashStorage.h>


//Can be changed based on the needs of the users
#define MOUSE_MOVER_XY 15                                             //Mouse move 
#define SWITCH_REACTION_TIME 50                                       //Minimum time for each switch action ( level 10 : 1x50 =50ms , level 1 : 10x50=500ms )
#define SWITCH_MODE_CHANGE_TIME 2000                                  //How long to hold switch 4 to change mode 

#define LED_BRIGHTNESS 150                                             //The mode led color brightness which is always on ( Use a low value to decrease power usage )
#define LED_ACTION_BRIGHTNESS 150                                      //The action led color brightness which can be a higher value than LED_BRIGHTNESS

//Define Mouse Actions
#define MOUSE_NO_ACTION 0 
#define MOUSE_MOVER_X 1
#define MOUSE_MOVER_Y 2
#define MOUSE_MOVER_LEFT_CLICK 3
#define MOUSE_MOVER_RIGHT_CLICK 4
#define MOUSE_MOVER_Y_UP 5
#define MOUSE_MOVER_X_RIGHT 6
#define MOUSE_MOVER_Y_DOWN 7
#define MOUSE_MOVER_X_LEFT 8

//Define Switch pins
#define LED_PIN 5
#define DOTSTAR_DATA_PIN    41
#define DOTSTAR_CLOCK_PIN   40

#define SWITCH_A_PIN 10
#define SWITCH_B_PIN 11
#define SWITCH_C_PIN 12
#define SWITCH_D_PIN 13

#define SWITCH_UP_PIN 7
#define SWITCH_RIGHT_PIN 9
#define SWITCH_DOWN_PIN A1
#define SWITCH_LEFT_PIN A0

// Variable Declaration

//Declare switch state variables for each switch
int switchAState;
int switchBState;
int switchCState;
int switchDState;

int switchUpState;
int switchRightState;
int switchDownState;
int switchLeftState;

bool previousSwitchAState = HIGH;
bool previousSwitchBState = HIGH;
bool previousSwitchCState = HIGH;
bool previousSwitchDState = HIGH;

bool previousSwitchUpState = HIGH;
bool previousSwitchRightState = HIGH;
bool previousSwitchDownState = HIGH;
bool previousSwitchLeftState = HIGH;

bool moverState[9] = {true,true,true,true,true,true,true,true};

//Stopwatches array used to time switch presses
StopWatch timeWatcher[3];
StopWatch switchDTimeWatcher[1];

//Declare Switch variables for settings 
int switchConfigured;
int switchReactionTime;
int switchReactionLevel;
int switchMode;

int morseReactionTime;

FlashStorage(switchConfiguredFlash, int);
FlashStorage(switchReactionLevelFlash, int);
FlashStorage(switchModeFlash, int);


//RGB LED Color code structure 

struct rgbColorCode {
    int r;    // red value 0 to 255
    int g;   // green value
    int b;   // blue value
 };

//Color structure 
typedef struct { 
  uint8_t colorNumber;
  String colorName;
  rgbColorCode colorCode;
} colorStruct;

 //Mode structure 
typedef struct { 
  uint8_t modeNumber;
  String modeName;
  uint8_t modeColorNumber;
} modeStruct;


 //Switch structure 
typedef struct { 
  uint8_t switchNumber;
  String switchName;
  uint8_t switchMouse;
  uint8_t switchColorNumber;
} switchStruct;


 //Settings Action structure 
typedef struct { 
  uint8_t settingsActionNumber;
  String settingsActionName;
  uint8_t settingsActionColorNumber;
} settingsActionStruct;

//Color properties 
const colorStruct colorProperty[] {
    {1,"Green",{0,50,0}},
    {2,"Pink",{50,00,20}},
    {3,"Yellow",{50,50,0}},    
    {4,"Orange",{50,20,0}},
    {5,"Blue",{0,0,50}},
    {6,"Red",{50,0,0}},
    {7,"Purple",{50,0,50}},
    {8,"Teal",{0,128,128}}       
};

//Switch properties 
const switchStruct switchProperty[] {
    {1,"Move-Y",MOUSE_MOVER_Y,5},                             
    {2,"Move-X",MOUSE_MOVER_X,6},                           
    {3,"Click-Left",MOUSE_MOVER_LEFT_CLICK,1},                             
    {4,"Click-Right",MOUSE_MOVER_RIGHT_CLICK,3},
    {5,"Move-Y-Up",MOUSE_MOVER_Y_UP,5},                             
    {6,"Move-X-Right",MOUSE_MOVER_X_RIGHT,6},                           
    {7,"Move-Y-Down",MOUSE_MOVER_Y_DOWN,5},                             
    {8,"Move-X-Left",MOUSE_MOVER_X_LEFT,6}                         
};



//Settings Action properties 
const settingsActionStruct settingsProperty[] {
    {1,"Increase Reaction",5},                             //{1=Increase Reaction,5=blue}
    {2,"Decrease Reaction",6},                             //{2=Decrease Reaction,6=red}
    {3,"Max Reaction",1},                                  //{3=Max Reaction,1=green}
    {4,"Min Reaction",1}                                   //{4=Min Reaction,1=green}
};

//Mode properties 
const modeStruct modeProperty[] {
    {1,"Mouse Mover",8},
    {2,"Settings",4}
};

//Setup NeoPixel LED
Adafruit_NeoPixel ledPixels = Adafruit_NeoPixel(1, LED_PIN, NEO_GRB + NEO_KHZ800);
Adafruit_DotStar dotStar(1, DOTSTAR_DATA_PIN, DOTSTAR_CLOCK_PIN, DOTSTAR_BRG);
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

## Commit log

2020-10-01 Added components list
    [Enabled_Controller_BOM.csv, Enabled_Controller_BOM.xlsx]
2020-10-01 Added PCB files
    [Enabled-Controller.brd, Enabled-Controller.sch]
2020-11-29 Added enclosure files
    [Enabled-Controller-Bottom.step, Enabled-Controller-Bottom.stl, Enabled-Controller-Top.stl]
2020-11-29 Updated Enclosure files for easy print
    [Enabled-Controller-Bottom.step, Enabled-Controller-Bottom.stl, Enabled-Controller-Top.stl]
2020-12-20 Updated BOM and added M2.5 screws
    [Enabled_Controller_BOM.csv, Enabled_Controller_BOM.xlsx]
2020-12-20 Redesigned the enclosure ( Snap fit )
    [Enabled-Controller-Bottom.step, Enabled-Controller-Bottom.stl, Enabled-Controller-Top.stl]
2020-12-23 Updated BOM for two versions
    [Enabled_Controller_BOM.csv, Enabled_Controller_BOM.xlsx]
2021-01-12 Updated enclosure files
    [Enabled-Controller-Bottom-Mount.step, Enabled-Controller-Bottom-Mount.stl, Enabled-Controller-Bottom.step, Enabled-Controller-Bottom.stl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]
2021-01-17 Updated Enclosure : Snap wall height was increased by 0.8mm.
    [Enabled-Controller-Bottom-Mount.step, Enabled-Controller-Bottom-Mount.stl, Enabled-Controller-Bottom.step, Enabled-Controller-Bottom.stl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]
2021-01-18 Updated BOM file : Price updated and changed screw part
    [Enabled_Controller_BOM.csv, Enabled_Controller_BOM.xlsx]
2021-01-18 Added the Assembly Instructions Manual
2021-01-18 Added PCB gerber files
2021-01-18 Moved the arduino code to new directory
2021-01-21 Updated Software : Fixed LED code and added more switch options
2021-01-25 Added Joystick Assembly
2021-01-31 Updated Assembly manual 1.11
2021-05-07 Removed old wireless code
2021-05-22 Added wireless version of Enabled Controller and added mouse mode
2021-06-07 Updated Eagle files
    [Enabled-Controller.brd, Enabled-Controller.sch]
2021-08-29 Added low power mode to wireless code
2021-08-29 Added updated PCB files
    [Enabled-Controller.brd, Enabled-Controller.sch]
2021-08-29 Updated enclosure for version 1.2
    [Enabled_Controller_Battery_Holder.step, Enabled_Controller_Battery_Holder.stl, Enabled_Controller_Bottom.step, Enabled_Controller_Bottom.stl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]
2021-08-29 Updated BOM Files
    [Enabled_Controller_BOM.csv, Enabled_Controller_BOM.xlsx, Enabled_Controller_USB_BOM.csv, Enabled_Controller_USB_BOM.xlsx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]
2021-08-29 Updated enclosure battery holder
    [Enabled_Controller_Battery_Holder.step, Enabled_Controller_Battery_Holder.stl, Enabled_Controller_Battery_Wall.step, Enabled_Controller_Battery_Wall.stl]
2021-10-01 Updated all files to version 1.2
    [Enabled_Controller_BOM.csv, Enabled_Controller_BOM.xlsx, Enabled_Controller_Battery_Holder.step, Enabled_Controller_Battery_Holder.stl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]

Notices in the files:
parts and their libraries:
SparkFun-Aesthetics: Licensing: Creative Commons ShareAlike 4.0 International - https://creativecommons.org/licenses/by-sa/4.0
